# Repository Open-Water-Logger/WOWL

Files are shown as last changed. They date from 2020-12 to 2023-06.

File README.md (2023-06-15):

# WOWL
Hardware and Software Resources for the Wireless Open Water Logger (WOWL). 

Most current version is Gen 3. A detailed description of the casting process can be found on our blog at https://openwaterlogger.org/.

WOWL is a project of Creare working in collaboration with the Darling Marine Center at UMaine.

This project is supported by NOAA via SBIR contract NA20OAR0210323.

This project is licensed under the Apache License 2.0

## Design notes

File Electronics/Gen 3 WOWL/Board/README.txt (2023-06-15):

Schematic
1010403-900-0011_SCH_REV-B.pdf = schematic drawing

BOM
1010403-900-0010_BOM_REV_B.pdf - list of parts needed to build assemblies

PCB/Board
1010403-900-0012_rev-B-Gerbers.zip = Files to have PCB manufactured.
1010403-900-0012_FAB-REV-B.pdf = Fabrication drawing showing drill, dimensions, and stack-up.
1010403-900-0012_PCB_Rev-B_Placement.txt = component XY coordinates needed for part placement.
1010403-900-0012_rev-b-IPC-2581.zip - files required to have boards built at CircuitHub.

Can live with PCB/Board
1010403-900-0013_ASSY-REV-B.pdf = Assembly print showing Top and bottom component placement.

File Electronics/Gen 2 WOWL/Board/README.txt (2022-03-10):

PCB/Board
1010403-900-0012_rev-a-Gerbers.zip = Files to have PCB manufactured.
1010403-900-0012_rev-a.brd = OrCAD Design file PCB.
1010403-900-0012_rev-a_fab.pdf = Fabrication drawing showing drill, dimensions, and stack-up.
1010403-900-0012_PCB_Rev-A_Placement.txt = component XY coordinates needed for part placement.

Can live with PCB/Board
1010403-900-0013_ASB_Rev-A.pdf = Assembly print showing Bottom component placement.
1010403-900-0013_AST_Rev-A.pdf = Assembly print showing Top component placement.

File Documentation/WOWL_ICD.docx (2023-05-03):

# WOWL Interface Control Document

# 1 Introduction

The WOWL is a submersible temperature and pressure sensor and data logger. When on the surface, it provides communication via a Bluetooth interface. This document describes that interface.

## CRC32

This technology makes use of the CRC32 algorithm in several places. This is based on the implementation given in the PNG standard:

https://www.w3.org/TR/PNG/#D-CRCAppendix

# 2 WOWL Service

The WOWL device provides the WOWL service, on UUID 0x3090. At this time, the service provides eight characteristics.

## Pressure Offset, in Millibars (0x3091)

This 8-bit unsigned value is added to the pressure measurement. It can be used to trick the WOWL into thinking it is submerged, which is useful in generating records for testing. NOTE: at this time, the radio stays on while the device is submerged. When this is not the case, this characteristic will be removed, so as to prevent the device from becoming incommunicative forever.

## Record Count (0x3092)

This field returns the number of records stored in non-volatile memory, as a u16.

## Measurement Results (0x3093)

If the host device registers for notifications on this UUID, it will receive the incoming data at a rate of once per 10 seconds when the device is surfaced, and neither downloading or erasing data. All data are in LSB. See Table 1. The data will come in chunks of 20 bytes each, padded with zeros as needed.

Table 1. WOWL Measurement Data Format
Data Item | Format | Units
Measurement Count | u32 | Measurements
Status | u32 | See Table 2
Reserved | u32 | N/A
Charging Voltage | f32 | volts
Charging Current | f32 | amps
Rectified Charging Coil Voltage | f32 | volts
Battery Voltage | f32 | volts
CPU Temperature | f32 | °C
Temperature via NTC | f32 | °C
Temperature via RTD | f32 | °C
Temperature from SI7051-A20-IMR Digital Temperature Sensor | f32 | °C
Pressure | f32 | mbar
Temperature from Pressure Sensor | f32 | °C
Temperature of NTC ADC | f32 | °C
Temperature of RTD ADC | f32 | °C
CRC32 of fields above | u32 | N/A
Characteristic Length | 64 bytes | --

NOTE: Be sure to de-register the notifications before disconnecting.

Table 2. WOWL Status Bitfield
Bit | Meaning if Set
0 | Charging
1-7 | RESERVED
8 | Firmware Operation Complete
9 | Firmware Operation Failed
10-15 | RESERVED
16 | Connected to BLE
17 | Advertising for BLE
18-22 | RESERVED
23 | Last Command Unsupported
24 | Flash Failure
25 | SI7051 Temperature Sensor Failure
26 | Spurious I²C Event
27 | Pressure Sensor Failure
28-31 | RESERVED

## Record Download Request (0x3094)

This characteristic specifies which records are transmitted when a download is requested.

Table 3. WOWL Download Request
Field | Format | Units
Offset | u16 | Records
Count | u16 | Records
Characteristic Length | 4 bytes | --

## Record Download Data (0x3095)

This characteristic receives the downloaded records, if set to transmit notifications.

Table 4. WOWL Download Data
Data Item | Format | Units
Record Index | u16 | Records
Record Status | u16 | See Table 5
Record Data | SAMPLE | See Table 1
Characteristic Length | 68 bytes | --

The ‘Record Status’ field contains the result of the record retrieval process.

Table 5. WOWL Record Read Error Codes
Code | Description
0 | No Error
1 | Device Error
2 | Record is Blank
3 | CRC Mismatch
4-65535 | RESERVED

Note that the CRC field of the Record Data does not include the Record Index or Record Status fields.

## Commands (0x3096)

This u8 characteristic receives user commands. It must be written with the WriteCharValue GATT operation, not WriteLongCharValue. The commands are queued, and will only take effect when the device is at standby (i.e., not busy or submerged). The exception is the RESET command which takes effect immediately.

Table 2. WOWL Commands
Code | Description
0 | RESERVED
1 | Commence Download
2 | Start Erasure of Records
3 | Reset Processor
4 | DFU Setup
5 | DFU Write
6 | DFU Reprogram
7-255 | RESERVED

## DFU Setup (0x3097)

This characteristic is used to inform the WOWL about an upcoming firmware upgrade. The fields are given below.

Table 4. WOWL DFU Setup Fields
Data Item | Format | Units
Firmware Length | u32 | Bytes
CRC32 | u32 | N/A
Characteristic Length | 8 bytes | --

## DFU Data (0x3098)

This characteristic is used to store blocks of the firmware file, for commit by the device to program memory. The entire block should be used.

# 3 Stored Data Download Procedure

Here are the steps to download data from the WOWL.

1) Determine the appropriate number of records to download per request. A number smaller than “all of them” may be more robust. The author has tested up to 16.
2) Connect to the device.
3) Consult the Record Count characteristic.
4) Set the Record Download Request characteristic with the offset (initially zero) and count (determined in step 0, trimmed to the value in step 2).
5) Request notifications for the Record Download Data characteristic.
6) Set the Command characteristic to 1.
7) Repeat steps 3 through 5, increasing the offset appropriately each iteration. If data does not match the provided checksum, or the Record Index falls out of synchronicity, request that record again with a side request for that offset, count of one.
8) Cancel notifications of the Record Download Data characteristic.
9) Disconnect from the device.

# 4 Device Firmware Update (DFU) Procedure

Enumerated below are the suggested steps for reprogramming the WOWL.

1) Connect to the device.
2) Update the DFU Setup characteristic with the size of the firmware and its CRC32.
3) Send the DFU Setup command.
4) Wait one second for the device to erase the temporary storage area.
5) Write the first data block to the DFU Data characteristic.
6) Send the DFU Write command.
7) Repeat steps 5 and 6 until all the firmware is written.
8) Send the DFU Reprogram command. If successful, the device will reset itself and the Bluetooth connection will be severed.
9) After a short wait the device will be available for reconnection.
10) The ‘Firmware Revision String’, part of the Device Information Service, at UUID 0x2A26, will contain the software build date and time.

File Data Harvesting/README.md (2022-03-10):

# Python WOWL downloader

Python script to download WOWL data ---> read_wowl.py.

read_wowl.py contains the functions that can connect to a WOWL and download the data. Sending data to server and location is currently not supported.

There seems to be a bug with the python bluetooth module (bleak) for Windows and code may error when connecting. We are working to fix this and it might run on other OS although it is untested.

More documentation and functionality for this code base will continue to be added.

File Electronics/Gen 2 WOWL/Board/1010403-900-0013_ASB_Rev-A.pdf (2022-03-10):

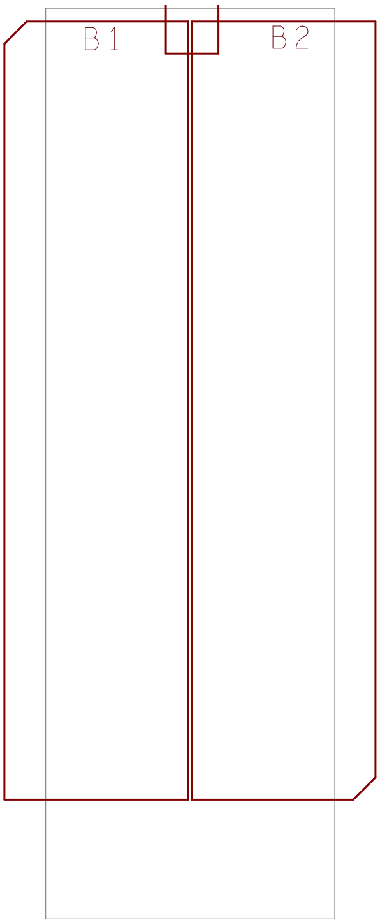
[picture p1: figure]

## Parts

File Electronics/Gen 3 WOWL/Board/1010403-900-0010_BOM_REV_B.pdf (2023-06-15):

WOWL Board Assembly/BOM
Project: | 1010403 Gone Fishing
Part #: | 1010403-900-0010 | Release 10/19/2022 RWM
Revision: | B
Item | Quantity | Reference | Description | Manufacturer | Manufacturer Part# | Suggested Vendor | Suggested Vendor Part # | Footprint | Temp Min | Temp Max
1 | 1 | DOC | Schematic | Creare | 1010403-900-0011, Rev.B | N/A | N/A | N/A | N/A | N/A
2 | 1 | PCB | PCB | | 1010403-900-0012, Rev.B | N/A | N/A | N/A | N/A | N/A
3 | 1 | ANT1 | PCB Antenna, 2.4GHz | DNP | DNP | DNP | DNP | pcbantenna_an043 | - | -
4 | 2 | B1 B2 | BATTERY NIMH 1.2V 700MAH AAA | Panasonic - BSG | HHR70AAAB8T | Digi-Key | P213T-ND | PANASONIC_HHR70AAAB8T | -10°C | 65°C
5 | 10 | C1 C4 C6 C10 C14 C15 C21 C40 C42 C55 0.1uF, 50V, 10%, X7R, Ceramic, 0402 | | TDK | CGA2B3X7R1H104K050BB | Digi-Key | 445-6899-1-ND | CAPC100X50X55L20N | -55°C | 125°C
6 | 1 | C2 | 10uF, 10V, 20%, X5R, Ceramic, 0402 | Samsung | CL05A106MP8NUB8 | Digi-Key | 1276-6830-1-ND | CAPC100X50X90L25N | -55°C | 85°C
7 | 1 | C11 | DNP, 10uF, 10V, 20%, X5R, Ceramic, 0402 | | | | | CAPC100X50X90L25N | -55°C | 85°C
8 | 1 | C12 | 22uF, 25V, 20%, X5R, Ceramic, 0805 | TDK Corporation | C2012X5R1E226M125AC | Digi-Key | 445-9112-1-ND | CAPC2013X145N | -55°C | 85°C
9 | 2 | C16 C58 | DNP, Capacitor, 0402 | NA | NA | NA | NA | CAPC1005X55L25N
10 | 1 | C19 | 0.8pF, 50V, ±0.1pF, NP0, Ceramic, 0402 | Murata | GJM1555C1HR80BB01D | Digi-Key | 490-6080-1-ND | CAPC100X50X55L25N | -55°C | 125°C
11 | 2 | C22 C25 | 22nF, 50V, 10%, X7R, Ceramic, 0402 | Murata Electronics North America GRM155R71H223KA12D | | Digi-Key | 490-3884-1-ND | CAPC100X50X55L25N | -55°C | 125°C
12 | 4 | C23 C24 C27 C28 | 12pF, 50V, 1%, NP0, Ceramic, 0402 | Murata | GJM1555C1H120FB01D | Digi-Key | 490-11190-1-ND | CAPC100X50X55L25N | -55°C | 125°C
13 | 2 | C26 C44 | 0.47uF, 25V, 10%, X5R, Ceramic, 0402 | TDK | C1005X5R1E474K050BB | Digi-Key | 445-8020-1-ND | CAPC100X50X55L15N | -55°C | 85°C
14 | 1 | C32 | 15nF, 100V, 10%, X7R, Ceramic, 0603 | Murata | GCM188R72A153KA37D | Digi-Key | 490-8029-1-ND | CAPC160X80X90L35N | -55°C | 125°C
15 | 3 | C41 C43 C56 | 1uF, 25V, 10%, X5R, Ceramic, 0603 | AVX | 06033D105KAT2A | Digi-Key | 478-5142-1-ND | CAPC1608X94N | -55°C | 85°C
16 | 2 | C45 C46 | 10nF, 50V, 10%, X8R, Ceramic, 0402 | TDK | C1005X8R1H103K050BB | Digi-Key | 445-8851-1-ND | CAPC100X50X55L15N | -55°C | 150°C
17 | 2 | C47 C48 | 68nF, 50V, 5%, X7R, Ceramic, 0603 | Kemet | C0603C683J5RACTU | Digi-Key | 399-9121-1-ND | CAPC160X80X87L35N | -55°C | 125°C
18 | 1 | C49 | 47nF, 50V, 10%, X7R, Ceramic, 0402 | TDK | CGA2B3X7R1H473K050BB | Digi-Key | 445-6897-1-ND | CAPC100X50X55L20N | -55°C | 125°C
19 | 1 | C50 | 1.8nF, 50V, 10%, X7R, Ceramic, 0402 | AVX | 04025C182KAT2A | Digi-Key | 478-1104-1-ND | CAPC100X50X56L25N | -55°C | 125°C
20 | 1 | C51 | 100pF, 50V, 5%, C0G, Ceramic, 0603 | KEMET | C0603T101J5GCLTU | Digi-Key | 399-6300-1-ND | CAPC160X80X87L35N | -55°C | 125°C
21 | 1 | C52 | 0.1uF, 50V, 10%, X7R, Ceramic, 0603 | AVX | 06035C104KAZ2A | Digi-Key | 478-3540-1-ND | CAPC1608X94N | -55°C | 125°C
22 | 2 | C53 C54 | 10uF, 35V, 20%, X5R, Ceramic, 0603 | Murata | GRM188R6YA106MA73D | Digi-Key | 490-13248-1-ND | CAPC160X80X100L37N | -55°C | 85°C
23 | 1 | C57 | 100pF, 50V, 1%, C0G, Ceramic, 0402 | AVX | 04025A101FAT2A | Digi-Key | 478-3658-1-ND | CAPC100X50X56L25N | -55°C | 125°C
24 | 1 | D1 | LED, Green, 2.1V, 20mA | SunLED | XZVG54W-8 | Digi-Key | 1497-1434-1-ND | LEDC200X125X120L40N | -40°C | 85°C
25 | 1 | D2 | LED Red/Yel, 2.2V/2V, 20mA, 1206 | SunLED | XZM2CRKCYK55W-8 | Digi-Key | 1497-1306-1-ND | SUNLED_XZM2CRKCYK55W-8 | -40°C | 85°C
26 | 1 | D3 | LED, Green, 2.1V, 10mA, 3.2mcd, 0603 | Lite-On Inc. | LTST-C190GKT | Digi-Key | 160-1183-1-ND | LEDC1608X80N | -55°C | 85°C
27 | 1 | F1 | Fuse, 2A, 63VDC, Slow, 1206 | Bourns | SF-1206SP200M-2 | Digi-Key | SF-1206SP200M-2CT-ND | FUSC320X160X117L51N | -55°C | 150°C
28 | 1 | J1 | FFC/FPC, 6pos, 0.5mm, 0.5A, 50V, R/A, SMD | Molex | 5034800600 | Digi-Key | WM1387CT-ND | Molex_503480-0600 | -40°C | 85°C
29 | 1 | L1 | 3.9nH, 400mA, High Frequency, 0402 | TDK | MLK1005S3N9ST000 | Digi-Key | 445-1462-1-ND | INDC1005X60L15 | -55°C | 125°C
30 | 1 | L2 | 10uH, 100mA, Wirewound, 0603 | Abracon | AISC-0603F-100J-T | Digi-Key | 535-12537-1-ND | Abracon_AISC-0603F | -40°C | 85°C
31 | 1 | L3 | 15nH, 300mA, High Frequency, 0402 | TDK | MLK1005S15NJT000 | Digi-Key | 445-1469-1-ND | INDC1005X60L15 | -55°C | 125°C
32 | 1 | Q2 | MOSFET, P-CH, 20V, 3.6A, SOT-23 | Diodes | DMP2035U-7 | Digi-Key | DMP2035U-7DICT-ND | SOT23-3P91_240X120L53X44 | -55°C | 150°C
33 | 1 | R1 | 100K, 1%, 50V, 1/16W, Thick, 0402 | Vishay | CRCW0402100KFKED | Digi-Key | 541-100KLCT-ND | RESC100X50X40L25 | -55°C | 155°C
34 | 1 | R2 | 4.99K, 1%, 50V, 1/16W, Thick, 0402 | Vishay | CRCW04024K99FKED | Digi-Key | 541-4.99KLCT-ND | RESC100X50X40L25 | -55°C | 155°C
35 | 1 | R4 | DNP, 4.99K, 1%, 50V, 1/16W, Thick, 0402 | | | | | RESC100X50X40L25 | -55°C | 155°C
36 | 1 | R5 | 140 Ohms, 1%, 75V, 1/10W, Thick, 0603 | Vishay | CRCW0603140RFKEA | Digi-Key | 541-140HCT-ND | RESC155X85X50L30N | -55°C | 155°C
37 | 4 | R7 R8 R9 R12 | 33 Ohms, 1%, 50V, 1/10W, Thick, 0402 | Panasonic | ERJ-2RKF33R0X | Digi-Key | P33.0LCT-ND | RESC100X50X40L25 | -55°C | 155°C
38 | 4 | R10 R19 R26 R33 | 10K, 1%, 50V, 1/10W, Thick, 0402 | Panasonic Electronic Components ERJ-2RKF1002X | | Digi-Key | P10.0KLCT-ND | RESC100X50X40L25 | -55°C | 155°C
39 | 4 | R11 R35 R36 R37 | 1M, 1%, 50V, 1/10W, Thick, 0402 | Panasonic | ERJ-2RKF1004X | Digi-Key | P1.00MLCT-ND | RESC100X50X40L25 | -55°C | 155°C
40 | 1 | R13 | DNP, Jumper, 50V, 1/16W, Thick, 0402 | Vishay | CRCW04020000Z0ED | Digi-Key | 541-0.0JCT-ND | RESC100X50X40L25 | -55°C | 155°C
41 | 1 | R14 | 10K, 1%, 50V, 1/16W, Thick, 0402 | Vishay | CRCW040210K0FKED | Digi-Key | 541-10.0KLCT-ND | RESC100X50X40L25 | -55°C | 155°C
42 | 1 | R15 | 357 Ohms, 1%, 75V, 1/10W, Thick, 0603 | Vishay | CRCW0603357RFKEA | Digi-Key | 541-357HCT-ND | RESC155X85X50L30N | -55°C | 155°C
43 | 1 | R16 | 1.5K, 5%, 75V, 1/10W, Thick, 0603 | Vishay | CRCW06031K50JNEA | Digi-Key | 541-1.5KGCT-ND | RESC155X85X50L30N | -55°C | 155°C
44 | 2 | R17 R20 | 1M, 1%, 50V, 1/16W, Thick, 0402 | KOA Speer | RK73H1ETTP1004F | Mouser | 660-RK73H1ETTP1004F | RESC1005X40N | -55°C | 155°C
45 | 3 | R22 R34 R39 | 100 Ohms, 1%, 50V, 1/10W, Thick, 0402 | Panasonic | ERJ-2RKF1000X | Digi-Key | P100LCT-ND | RESC100X50X40L25 | -55°C | 155°C
46 | 1 | R30 | 140K, 1%, 50V, 1/10W, Thick, 0402 | Panasonic | ERJ-2RKF1403X | Digi-Key | P140KLCT-ND | RESC100X50X40L25 | -55°C | 155°C
47 | 1 | R31 | 100K, 1%, 50V, 1/10W, Thick, 0402 | Panasonic | ERJ-2RKF1003X | Digi-Key | P100KLCT-ND | RESC100X50X40L25 | -55°C | 155°C
48 | 1 | R38 | DNP, 100K, 1%, 150V, 1/8W, Thick, 0805 | Vishay | DNP(CRCW0805100KFKEA) | | | RESC205X125X50L35N | -55°C | 155°C
49 | 2 | R44 R45 | 4.02K, 1%, 50V, 1/10W, Thick, 0402 | Panasonic | ERJ-2RKF4021X | Digi-Key | P4.02KLCT-ND | RESC100X50X40L25 | -55°C | 155°C
50 | 1 | R51 | Jumper, 50V, 1/16W, Thick, 0402 | Vishay | CRCW04020000Z0ED | Digi-Key | 541-0.0JCT-ND | RESC100X50X40L25 | -55°C | 155°C
51 | 1 | RT2 | Thermistor, NTC, 10K, Max Temp 125°C,TH | Cantherm | MF52A2103J3470 | Digi-Key | 317-1258-ND | THRMRB220W45L300T300H950 | -55°C | 125°C
52 | 1 | SW1 | Switch, Reed, SPST-NO, 100mA, 30V, SM | Standex | MK24-A-3 | Digi-Key | 374-1138-1-ND | standex_mk24-a-3 | -40°C | 115°C
53 | 12 | TP7 TP8 TP9 TP12 TP19 TP20 TP21 TP23 TP24 TP25 TP26 TP27 DNP, Test Point, SMD, 25 mil Round Pad | | NA | NA | NA | NA | TP_C0635 | NA | NA
54 | 2 | TP28 TP29 | Test Point, Miniature, 3.4mm x 1.8mm Pad, SMD | Keystone | 5015 | Digi-Key | 36-5015CT-ND | TP340X180N
55 | 1 | U1 | Temperature, Digital, -40~125°C, 6WDFN | TI | TMP117AIDRVR | Digi-Key | 296-51834-1-ND | son7p65_200x200x80l25x30t160x100n-55°C | | 150°C
56 | 1 | U10 | Buffer, Triple, Open Drain, 8XSON | Nexperia USA Inc. | 74LVC3G07GS,115 | Digi-Key | 1727-8082-1-ND | PSON8P35_135X100X35L31X16N | -40°C | 125°C
57 | 1 | U2 | Pressure Sensor, 0 ~30bar, ±400 mbar, I2C, SMD | TE Connectivity Measurement Specialties MS583730BA01-50 | | Digi-Key | 223-1704-1-ND | icdfn4_330x330x285l130x130 | -20°C | 85°C
58 | 1 | U3 | Buffer, Single, Open Drain, 6-SON | TI | SN74LVC1G07QDRYRQ1 | Digi-Key | 296-SN74LVC1G07QDRYRQ1CT-ND pson6p50_145x100x55l30x20n | | -40°C | 125°C
59 | 1 | U5 | SOC, 2.4 GHz Bluetooth, Cortex M4 MCU, 512K Flash, 64K RAM, 48QFN Nordic | | NRF52832-QFAA-R | Digi-Key | 1490-1052-1-ND | QFN40P600X600X90-49N | -40°C | 85°C
60 | 1 | U6 | Flash Memory, 16Mbit, 80MHz, 8USON | Macronix | MX25R1635FZUIH0 | Digi-Key | 1092-1178-1-ND | PSON9P50_200X300X60L40X25T160X20N -40°C | | 85°C
61 | 1 | U7 | Battery Charger, Multi-Chemistry, 60V, 250mA, 10DFN Analog Devices Inc. | | LTC4079EDD#TRPBF | Digi-Key | LTC4079EDD#TRPBFCT-ND | SON11P50_300X300X80L40X25T238X165N -40°C | | 125°C
62 | 1 | U8 | Wireless Power Supply Receiver, 20QFN | Texas Instruments | BQ51013ARHLR | Digi-Key | 296-30568-1-ND | QFN50P450X350X100-21N | 0°C | 125°C
63 | 1 | U9 | Opamp, Single, GP, RRIO, 6.2kHz, SC70-5 | Texas Instruments | LPV521MG/NOPB | Digi-Key | 296-39069-1-ND | SOT23-5P65_210X110L36X22N | -40°C | 125°C
64 | 1 | Y2 | Crystal, 32MHz, 8pF, SMD | ECS | ECS-320-8-37CKM | Digi-Key | XC1547CT-ND | OSCCC200X160X46-4NA | -20°C | 70°C
65 | 1 | Y4 | Crystal, 32.768kHz, 9pF, SMD | Abracon | ABS05-32.768KHZ-9-T | Digi-Key | 535-11897-1-ND | DFN160X100X50-2NA | -40°C | 85°C
66 | 1 | L4 | Coil | TDK | WR303050-15F5-G | Digi-Key | 445-16092-ND | N/A

Part Supplied by Creare
DNP = Do Not Populate
Additional Assembly Required/Part Supplied by Creare
WOWL Board Assembly/BOM | Page 1 of 1

1010403-900-0010
Rev. B

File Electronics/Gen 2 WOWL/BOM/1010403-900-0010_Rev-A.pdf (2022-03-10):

WOWL Board Assembly/BOM
Project: | 1010403 Gone Fishing
Part #: | 1010403-900-0010 | Released 02/22/2022 RWM
Revision: | A
Item | Quantity | Reference | Description | Manufacturer | Manufacturer Part# | Suggested Vendor | Suggested Vendor Part # | Footprint | Temp Min | Temp Max
1 | 1 | DOC | Schematic | Creare | 1010403-900-0011, Rev.A | N/A | N/A | N/A | N/A | N/A
2 | 1 | PCB | PCB | | 1010403-900-0012, Rev.A | N/A | N/A | N/A | N/A | N/A
3 | 1 | ANT1 | PCB Antenna, 2.4GHz | DNP | DNP | DNP | DNP | pcbantenna_an043 | - | -
4 | 2 | B1 B2 | BATTERY NIMH 1.2V 700MAH AAA | Panasonic - BSG | HHR70AAAB8T | Digi-Key | P213T-ND | PANASONIC_HHR70AAAB8T | -10°C | 65°C
5 | 15 | C1 C3 C4 C5 C7 C8 C10 C12 C13 C14 C15 C40 C42 C43 C55 | 0.1uF, 50V, 10%, X7R, Ceramic, 0402 | TDK | CGA2B3X7R1H104K050BB | Digi-Key | 445-6899-1-ND | CAPC100X50X55L20N | -55°C | 125°C
6 | 1 | C2 | 10uF, 10V, 20%, X5R, Ceramic, 0402 | Samsung | CL05A106MP8NUB8 | Digi-Key | 1276-6830-1-ND | CAPC100X50X90L25N | -55°C | 85°C
7 | 1 | C11 | DNP 10uF, 10V, 20%, X5R, Ceramic, 0402 | Samsung | CL05A106MP8NUB8 | Digi-Key | 1276-6830-1-ND | CAPC100X50X90L25N | -55°C | 85°C
8 | 1 | C6 | 4.7uF, 10V, 10%, X5R, Ceramic, 0402 | Murata | ZRB15XR61A475KE01D | Digi-Key | 490-13252-1-ND | CAPC100X50X80L25N | -55°C | 85°C
9 | 1 | C9 | 4.7uF, 10V, 10%, X5R, Ceramic, 0402 | TDK | C1005X5R1A475K050BC | Digi-Key | 445-13820-1-ND | CAPC102X52X65L15N | -55°C | 85°C
10 | 1 | C16 | 3.4pF, 50V, ±0.1pF, C0G, Ceramic, 0402 | KEMET | CBR04C349B5GAC | Digi-Key | 399-16077-1-ND | CAPC100X50X55L22N | -55°C | 125°C
11 | 1 | C17 | 0.22uF, 35V, 10%, X7R, Ceramic, 0402 | TDK | C1005X7R1V224K050BE | Digi-Key | 445-173778-1-ND | CAPC100X50X60L15N | -55°C | 125°C
12 | 1 | C18 | 1.2PF, 50V, ±0.05pF, C0G, Ceramic, 0402 | Murata | GJM1555C1H1R2WB01D | Digi-Key | 490-11195-1-ND | CAPC100X50X55L25N | -55°C | 125°C
13 | 1 | C19 | 0.5pF, 50V, ±0.1pF, C0G, Ceramic, 0402 | Murata | GJM1555C1HR50BB01D | Digi-Key | 490-6077-1-ND | CAPC100X50X55L25N | -55°C | 125°C
14 | 2 | C20 C21 | DNP, 1uF, 10V, 10%, X7S, Ceramic, 0402 | TDK | C1005X7S1A105K050BC | Digi-Key | 445-9116-1-ND | CAPC100X50X55L15N | -55°C | 125°C
15 | 2 | C22 C25 | 22nF, 50V, 10%, X7R, Ceramic, 0402 | Murata Electronics North America GRM155R71H223KA12D | | Digi-Key | 490-3884-1-ND | CAPC100X50X55L25N | -55°C | 125°C
16 | 2 | C23 C24 | DNP 12pF, 50V, 1%, NP0, Ceramic, 0402 | Murata | GJM1555C1H120FB01D | Digi-Key | 490-11190-1-ND | CAPC100X50X55L25N | -55°C | 125°C
17 | 2 | C27 C28 | 12pF, 50V, 1%, NP0, Ceramic, 0402 | Murata | GJM1555C1H120FB01D | Digi-Key | 490-11190-1-ND | CAPC100X50X55L25N | -55°C | 125°C
18 | 2 | C26 C44 | 0.47uF, 25V, 10%, X5R, Ceramic, 0402 | TDK | C1005X5R1E474K050BB | Digi-Key | 445-8020-1-ND | CAPC100X50X55L15N | -55°C | 85°C
19 | 1 | C32 | 15nF, 100V, 10%, X7R, Ceramic, 0603 | Murata | GCM188R72A153KA37D | Digi-Key | 490-8029-1-ND | CAPC160X80X90L35N | -55°C | 125°C
20 | 1 | C41 | 1uF, 25V, 10%, X5R, Ceramic, 0603 | AVX Corporation | 06033D105KAT2A | Digi-Key | 478-5142-1-ND | CAPC1608X94N | -55°C | 85°C
21 | 2 | C45 C46 | 10nF, 50V, 10%, X8R, Ceramic, 0402 | TDK Corporation | C1005X8R1H103K050BB | Digi-Key | 445-8851-1-ND | CAPC100X50X55L15N | -55°C | 150°C
22 | 2 | C47 C48 | 68nF, 50V, 5%, X7R, Ceramic, 0603 | Kemet | C0603C683J5RACTU | Digi-Key | 399-9121-1-ND | CAPC160X80X87L35N | -55°C | 125°C
23 | 1 | C49 | 47nF, 50V, 10%, X7R, Ceramic, 0402 | TDK | CGA2B3X7R1H473K050BB | Digi-Key | 445-6897-1-ND | CAPC100X50X55L20N | -55°C | 125°C
24 | 1 | C50 | 1.8nF, 50V, 10%, X7R, Ceramic, 0402 | AVX | 04025C182KAT2A | Digi-Key | 478-1104-1-ND | CAPC100X50X56L25N | -55°C | 125°C
25 | 1 | C51 | 100pF, 50V, 5%, C0G, Ceramic, 0603 | KEMET | C0603T101J5GCLTU | Digi-Key | 399-6300-1-ND | CAPC160X80X87L35N | -55°C | 125°C
26 | 1 | C52 | 0.1uF, 50V, 10%, X7R, Ceramic, 0603 | AVX | 06035C104KAZ2A | Digi-Key | 478-3540-1-ND | CAPC1608X94N | -55°C | 125°C
27 | 2 | C53 C54 | 10uF, 35V, 20%, X5R, Ceramic, 0603 | Murata | GRM188R6YA106MA73D | Digi-Key | 490-13248-1-ND | CAPC160X80X100L37N | -55°C | 85°C
28 | 1 | D1 | LED, Green, 2.1V, 20mA | SunLED | XZVG54W-8 | Digi-Key | 1497-1434-1-ND | LEDC200X125X120L40N | -40°C | 85°C
29 | 1 | D2 | LED Red/Yel, 2.2V/2V, 20mA, 1206 | SunLED | XZM2CRKCYK55W-8 | Digi-Key | 1497-1306-1-ND | SUNLED_XZM2CRKCYK55W-8 | -40°C | 85°C
30 | 1 | D3 | LED, Green, 2.1V, 10mA, 3.2mcd, 0603 | Lite-On Inc. | LTST-C190GKT | Digi-Key | 160-1183-1-ND | LEDC1608X80N | -55°C | 85°C
31 | 1 | F1 | DNP Fuse, 2A, 63VDC, Slow, 1206 | Bourns | SF-1206SP200M-2 | Digi-Key | SF-1206SP200M-2CT-ND | FUSC320X160X117L51N | -55°C | 150°C
32 | 1 | J1 | FFC/FPC, 6pos, 0.5mm, 0.5A, 50V, R/A, SMD | Molex | 5034800600 | Digi-Key | WM1387CT-ND | Molex_503480-0600 | -40°C | 85°C
33 | 1 | L1 | 3.3nH, 2A, High Freq., Wirewound, 0402 | Murata | LQW15AN3N3B80D | Digi-Key | 490-7641-1-ND | INDC100X60X60L20N | -55°C | 125°C
34 | 1 | L2 | 22nH, 350mA, High Frequency, 0402 | Murata | LQG15HS22NH02D | Digi-Key | 490-15112-1-ND | INDC100X50X55L25N | -55°C | 125°C
35 | 1 | L3 | 10uH, 200mA, 1.2 OHM, 0603 | KEMET | L0603B100KPWFT | Digi-Key | 399-17789-1-ND | indc160x80x90l35n | -40°C | 105°C
36 | 1 | Q2 | MOSFET, P-CH, 20V, 3.6A, SOT-23 | Diodes | DMP2035U-7 | Digi-Key | DMP2035U-7DICT-ND | SOT23-3P91_240X120L53X44 | -55°C | 150°C
37 | 1 | R1 | DNP, 100K, 1%, 150V, 1/8W, Thick, 0805 | Vishay | DNP(CRCW0805100KFKEA) | | | RESC205X125X50L35N | -55°C | 155°C
38 | 1 | R2 | 100K, 1%, 50V, 1/16W, Thick, 0402 | Vishay | CRCW0402100KFKED | Digi-Key | 541-100KLCT-ND | RESC100X50X40L25 | -55°C | 155°C
39 | 1 | R3 | 4.99K, 1%, 50V, 1/16W, Thick, 0402 | Vishay | CRCW04024K99FKED | Digi-Key | 541-4.99KLCT-ND | RESC100X50X40L25 | -55°C | 155°C
40 | 1 | R4 | 4.99K, 1%, 50V, 1/16W, Thick, 0402 | Vishay | CRCW04024K99FKED | Digi-Key | 541-4.99KLCT-ND | RESC100X50X40L25 | -55°C | 155°C
41 | 1 | R5 | 140 Ohms, 1%, 75V, 1/10W, Thick, 0603 | Vishay Dale | CRCW0603140RFKEA | Digi-Key | 541-140HCT-ND | RESC1609X50N | -55°C | 155°C
42 | 1 | R6 | Jumper, 50V, 1.5A, Thick, 0402 | Stackpole | RMCF0402ZT0R00 | Digi-Key | RMCF0402ZT0R00CT-ND | RESC100X50X40L25 | -55°C | 155°C
43 | 4 | R7 R8 R9 R12 | 33 Ohms, 1%, 50V, 1/10W, Thick, 0402 | Panasonic | ERJ-2RKF33R0X | Digi-Key | P33.0LCT-ND | RESC100X50X40L25 | -55°C | 155°C
44 | 4 | R10 R19 R26 R33 | 10K, 1%, 50V, 1/10W, Thick, 0402 | Panasonic Electronic Components ERJ-2RKF1002X | | Digi-Key | P10.0KLCT-ND | RESC100X50X40L25 | -55°C | 155°C
45 | 4 | R11 R35 R36 R37 | 1M, 1%, 50V, 1/10W, Thick, 0402 | Panasonic | ERJ-2RKF1004X | Digi-Key | P1.00MLCT-ND | RESC100X50X40L25 | -55°C | 155°C
46 | 1 | R13 | DNP, Jumper, 50V, 1/16W, Thick, 0402 | Vishay | CRCW04020000Z0ED | Digi-Key | 541-0.0JCT-ND | RESC100X50X40L25 | -55°C | 155°C
47 | 1 | R14 | 10K, 1%, 50V, 1/16W, Thick, 0402 | Vishay | CRCW040210K0FKED | Digi-Key | 541-10.0KLCT-ND | RESC100X50X40L25 | -55°C | 155°C
48 | 1 | R15 | 357 Ohms, 1%, 75V, 1/10W, Thick, 0603 | Vishay | CRCW0603357RFKEA | Digi-Key | 541-357HCT-ND | RESC155X85X50L30N | -55°C | 155°C
49 | 1 | R16 | 1.5K, 5%, 75V, 1/10W, Thick, 0603 | Vishay Dale | CRCW06031K50JNEA | Digi-Key | 541-1.5KGCT-ND | RESC1609X50N | -55°C | 155°C

Part Supplied by Creare
DNP = Do Not Populate
WOWL Board Assembly/BOM | Page 1 of 2

1010403-900-0010
Rev. A

50 | 2 | R17 R20 | 1M, 1%, 50V, 1/16W, Thick, 0402 | KOA Speer | RK73H1ETTP1004F | Mouser | 660-RK73H1ETTP1004F | RESC1005X40N | -55°C | 155°C
51 | 3 | R22 R34 R39 | 100 Ohms, 1%, 50V, 1/10W, Thick, 0402 | Panasonic | ERJ-2RKF1000X | Digi-Key | P100LCT-ND | RESC100X50X40L25 | -55°C | 155°C
52 | 1 | R30 | 140K, 1%, 50V, 1/10W, Thick, 0402 | Panasonic | ERJ-2RKF1403X | Digi-Key | P140KLCT-ND | RESC100X50X40L25 | -55°C | 155°C
53 | 1 | R31 | 100K, 1%, 50V, 1/10W, Thick, 0402 | Panasonic | ERJ-2RKF1003X | Digi-Key | P100KLCT-ND | RESC100X50X40L25 | -55°C | 155°C
54 | 2 | R44 R45 | 4.02K, 1%, 50V, 1/10W, Thick, 0402 | Panasonic | ERJ-2RKF4021X | Digi-Key | P4.02KLCT-ND | RESC100X50X40L25 | -55°C | 155°C
55 | 1 | RT2 | Thermistor, NTC, 10K, Max Temp 125°C,TH | Cantherm | MF52A2103J3470 | Digi-Key | 317-1258-ND | THRMRB220W45L300T300H950 | -55°C | 125°C
56 | 1 | SW1 | Switch, Reed, SPST-NO, 100mA, 30V, SM | Standex | MK24-A-3 | Digi-Key | 374-1138-1-ND | standex_mk24-a-3 | -40°C | 115°C
57 | 12 | TP1 TP2 TP3 TP7 | DNP, Test Point, SMD, 25 mil Round Pad | NA | NA | NA | NA | TP_C0635
58 | 2 | TP28 TP29 | Test Point, Miniature, 3.4mm x 1.8mm Pad, SMD | Keystone | 5015 | Digi-Key | 36-5015CT-ND | TP340X180N
59 | 1 | U1 | Temperature, Digital, -40~125°C, 6WDFN | TI | TMP117AIDRVR | Digi-Key | 296-51834-1-ND | son7p65_200x200x80l25x30t160x100n-55°C | | 150°C
60 | 1 | U10 | Buffer, Triple, Open Drain, 8XSON | Nexperia USA Inc. | 74LVC3G07GS,115 | Digi-Key | 1727-8082-1-ND | PSON8P35_135X100X35L31X16N | -40°C | 125°C
61 | 1 | U2 | Pressure Sensor, 0 ~30bar, ±400 mbar, I2C, SMD | TE Connectivity Measurement Specialties MS583730BA01-50 | | Digi-Key | 223-1704-1-ND | icdfn4_330x330x285l130x130 | -20°C | 85°C
62 | 1 | U3 | RF Filter, Low Pass, 2.45GHZ Center, 4SMD | TDK | DLF162500LT-5028A1 | Digi-Key | 445-15658-1-ND | tdk_dlf162500lt-5028a1 | -40°C | 85°C
63 | 1 | U4 | IC BUFFER NON-INVERT 5.5V 6USON | TI | SN74LVC1G07QDRYRQ1 | Digi-Key | 296-SN74LVC1G07QDRYRQ1CT-NDpson6p50_145x100x55l30x20n | -40C ~ 125C (TA)
64 | 1 | U5 | SOC, 2.4 GHz Bluetooth, Cortex-M0+ MCU, 256K Flash, 64K RAM, 48QFN STMicro | | BLUENRG-355MT | Mouser | 511-BLUENRG-355MT | QFN49P40_600X600X105L40X21T450N-40°C | | 105°C
65 | 1 | U6 | Flash Memory, 16Mbit, 80MHz, 8USON | Macronix | MX25R1635FZUIH0 | Digi-Key | 1092-1178-1-ND | PSON9P50_200X300X60L40X25T160X20N -40°C | | 85°C
66 | 1 | U7 | Battery Charger, Multi-Chemistry, 60V, 250mA, 10DFN Analog Devices Inc. | | LTC4079EDD#TRPBF | Digi-Key | LTC4079EDD#TRPBFCT-ND | SON11P50_300X300X80L40X25T238X165N -40°C | | 125°C
67 | 1 | U8 | Wireless Power Supply Receiver, 20QFN | Texas Instruments | BQ51013ARHLR | Digi-Key | 296-30568-1-ND | QFN50P450X350X100-21N | 0°C | 125°C
68 | 1 | U9 | Opamp, Single, GP, RRIO, 6.2kHz, SC70-5 | Texas Instruments | LPV521MG/NOPB | Digi-Key | 296-39069-1-ND | SOT23-5P65_210X110L36X22N | -40°C | 125°C
69 | 1 | Y2 | Crystal, 32MHz, 8pF, SMD | ECS | ECS-320-8-37CKM | Digi-Key | XC1547CT-ND | OSCCC200X160X46-4NA | -20°C | 70°C
70 | 1 | Y4 | Crystal, 32.768kHz, 9pF, SMD | Abracon | ABS05-32.768KHZ-9-T | Digi-Key | 535-11897-1-ND | DFN160X100X50-2NA | -40°C | 85°C
71 | 1 | L4 | Coil | TDK | WR303050-15F5-G | Digi-Key | 445-16092-ND | N/A
WOWL Board Assembly/BOM | Page 2 of 2

1010403-900-0010
Rev. A

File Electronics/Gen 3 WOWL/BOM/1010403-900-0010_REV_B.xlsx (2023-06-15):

WOWL Board Assembly/BOM
Project: | WOWL
Part #: | 1010403-900-0010 |  | Release 10/19/2022 RWM
Revision: | B
Item | Quantity | Reference | Description | Manufacturer | Manufacturer Part# | Suggested Vendor | Suggested Vendor Part # | Footprint | Temp Min | Temp Max
1 | 1 | DOC | Schematic | Creare | 1010403-900-0011, Rev.B | N/A | N/A | N/A | N/A | N/A
2 | 1 | PCB | PCB |  | 1010403-900-0012, Rev.B | N/A | N/A | N/A | N/A | N/A
3 | 1 | ANT1 | PCB Antenna, 2.4GHz | DNP | DNP | DNP | DNP | pcbantenna_an043 | - | - |  | TMP-5069
4 | 2 | B1 B2 | BATTERY NIMH 1.2V 700MAH AAA | Panasonic - BSG | HHR70AAAB8T | Digi-Key | P213T-ND | PANASONIC_HHR70AAAB8T | -10°C | 65°C | 27 | HHR70AAAB8T
5 | 10 | C1 C4 C6 C10 C14 C15 C21 C40 C42 C55 | 0.1uF, 50V, 10%, X7R, Ceramic, 0402 | TDK | CGA2B3X7R1H104K050BB | Digi-Key | 445-6899-1-ND | CAPC100X50X55L20N | -55°C | 125°C | 1427408 | CGA2B3X7R1H104K050BB
6 | 1 | C2 | 10uF, 10V, 20%, X5R, Ceramic, 0402 | Samsung | CL05A106MP8NUB8 | Digi-Key | 1276-6830-1-ND | CAPC100X50X90L25N | -55°C | 85°C | 3619004 | CL05A106MP8NUB8
7 | 1 | C11 | DNP, 10uF, 10V, 20%, X5R, Ceramic, 0402 |  |  |  |  | CAPC100X50X90L25N | -55°C | 85°C |  | DNP
8 | 1 | C12 | 22uF, 25V, 20%, X5R, Ceramic, 0805 | TDK Corporation | C2012X5R1E226M125AC | Digi-Key | 445-9112-1-ND | CAPC2013X145N | -55°C | 85°C | 0 | C2012X5R1E226M125AC
9 | 2 | C16 C58 | DNP, Capacitor, 0402 | NA | NA | NA | NA | CAPC1005X55L25N |  |  |  | DNP_CAP_0402
10 | 1 | C19 | 0.8pF, 50V, ±0.1pF, NP0, Ceramic, 0402 | Murata | GJM1555C1HR80BB01D | Digi-Key | 490-6080-1-ND | CAPC100X50X55L25N | -55°C | 125°C | 266571 | GJM1555C1HR80BB01D
11 | 2 | C22 C25 | 22nF, 50V, 10%, X7R, Ceramic, 0402 | Murata Electronics North America | GRM155R71H223KA12D | Digi-Key | 490-3884-1-ND | CAPC100X50X55L25N | -55°C | 125°C | 2638 | GRM155R71H223KA12D
12 | 4 | C23 C24 C27 C28 | 12pF, 50V, 1%, NP0, Ceramic, 0402 | Murata | GJM1555C1H120FB01D | Digi-Key | 490-11190-1-ND | CAPC100X50X55L25N | -55°C | 125°C | 28705807 | GJM1555C1H120FB01D
13 | 2 | C26 C44 | 0.47uF, 25V, 10%, X5R, Ceramic, 0402 | TDK | C1005X5R1E474K050BB | Digi-Key | 445-8020-1-ND | CAPC100X50X55L15N | -55°C | 85°C | 522 | C1005X5R1E474K050BB
14 | 1 | C32 | 15nF, 100V, 10%, X7R, Ceramic, 0603 | Murata | GCM188R72A153KA37D | Digi-Key | 490-8029-1-ND | CAPC160X80X90L35N | -55°C | 125°C | 24561 | GCM188R72A153KA37D
15 | 3 | C41 C43 C56 | 1uF, 25V, 10%, X5R, Ceramic, 0603 | AVX | 06033D105KAT2A | Digi-Key | 478-5142-1-ND | CAPC1608X94N | -55°C | 85°C | 396328 | 06033D105KAT2A
16 | 2 | C45 C46 | 10nF, 50V, 10%, X8R, Ceramic, 0402 | TDK | C1005X8R1H103K050BB | Digi-Key | 445-8851-1-ND | CAPC100X50X55L15N | -55°C | 150°C | 2503 | C1005X8R1H103K050BB
17 | 2 | C47 C48 | 68nF, 50V, 5%, X7R, Ceramic, 0603 | Kemet | C0603C683J5RACTU | Digi-Key | 399-9121-1-ND | CAPC160X80X87L35N | -55°C | 125°C | 12690 | C0603C683J5RACTU
18 | 1 | C49 | 47nF, 50V, 10%, X7R, Ceramic, 0402 | TDK | CGA2B3X7R1H473K050BB | Digi-Key | 445-6897-1-ND | CAPC100X50X55L20N | -55°C | 125°C | 3520015 | CGA2B3X7R1H473K050BB
19 | 1 | C50 | 1.8nF, 50V, 10%, X7R, Ceramic, 0402 | AVX | 04025C182KAT2A | Digi-Key | 478-1104-1-ND | CAPC100X50X56L25N | -55°C | 125°C | 105451 | 04025C182KAT2A
20 | 1 | C51 | 100pF, 50V, 5%, C0G, Ceramic, 0603 | KEMET | C0603T101J5GCLTU | Digi-Key | 399-6300-1-ND | CAPC160X80X87L35N | -55°C | 125°C | 6469 | C0603T101J5GCLTU
21 | 1 | C52 | 0.1uF, 50V, 10%, X7R, Ceramic, 0603 | AVX | 06035C104KAZ2A | Digi-Key | 478-3540-1-ND | CAPC1608X94N | -55°C | 125°C | 2267120 | 06035C104KAZ2A
22 | 2 | C53 C54 | 10uF, 35V, 20%, X5R, Ceramic, 0603 | Murata | GRM188R6YA106MA73D | Digi-Key | 490-13248-1-ND | CAPC160X80X100L37N | -55°C | 85°C | 799215 | GRM188R6YA106MA73D
23 | 1 | C57 | 100pF, 50V, 1%, C0G, Ceramic, 0402 | AVX | 04025A101FAT2A | Digi-Key | 478-3658-1-ND | CAPC100X50X56L25N | -55°C | 125°C | 353589 | 04025A101FAT2A
24 | 1 | D1 | LED, Green, 2.1V, 20mA | SunLED | XZVG54W-8 | Digi-Key | 1497-1434-1-ND | LEDC200X125X120L40N | -40°C | 85°C | 12030 | XZVG54W-8
25 | 1 | D2 | LED Red/Yel, 2.2V/2V, 20mA, 1206 | SunLED | XZM2CRKCYK55W-8 | Digi-Key | 1497-1306-1-ND | SUNLED_XZM2CRKCYK55W-8 | -40°C | 85°C | 6541 | XZM2CRKCYK55W-8
26 | 1 | D3 | LED, Green, 2.1V, 10mA, 3.2mcd, 0603 | Lite-On Inc. | LTST-C190GKT | Digi-Key | 160-1183-1-ND | LEDC1608X80N | -55°C | 85°C | 790591 | LTST-C190GKT
27 | 1 | F1 | Fuse, 2A, 63VDC, Slow, 1206 | Bourns | SF-1206SP200M-2 | Digi-Key | SF-1206SP200M-2CT-ND | FUSC320X160X117L51N | -55°C | 150°C | 3630 | SF-1206SP200M-2
28 | 1 | J1 | FFC/FPC, 6pos, 0.5mm, 0.5A, 50V, R/A, SMD | Molex | 5034800600 | Digi-Key | WM1387CT-ND | Molex_503480-0600 | -40°C | 85°C | 47873 | 503480-0600
29 | 1 | L1 | 3.9nH, 400mA, High Frequency, 0402 | TDK | MLK1005S3N9ST000 | Digi-Key | 445-1462-1-ND | INDC1005X60L15 | -55°C | 125°C | 41815 | MLK1005S3N9ST000
30 | 1 | L2 | 10uH, 100mA, Wirewound, 0603 | Abracon | AISC-0603F-100J-T | Digi-Key | 535-12537-1-ND | Abracon_AISC-0603F | -40°C | 85°C | 5900 | AISC-0603F-100J-T
31 | 1 | L3 | 15nH, 300mA, High Frequency, 0402 | TDK | MLK1005S15NJT000 | Digi-Key | 445-1469-1-ND | INDC1005X60L15 | -55°C | 125°C | 42575 | MLK1005S15NJT000
32 | 1 | Q2 | MOSFET, P-CH, 20V, 3.6A, SOT-23 | Diodes | DMP2035U-7 | Digi-Key | DMP2035U-7DICT-ND | SOT23-3P91_240X120L53X44 | -55°C | 150°C | 0 | DMP2035U-7
33 | 1 | R1 | 100K, 1%, 50V, 1/16W, Thick, 0402 | Vishay | CRCW0402100KFKED | Digi-Key | 541-100KLCT-ND | RESC100X50X40L25 | -55°C | 155°C | 7 | CRCW0402100KFKED
34 | 1 | R2 | 4.99K, 1%, 50V, 1/16W, Thick, 0402 | Vishay | CRCW04024K99FKED | Digi-Key | 541-4.99KLCT-ND | RESC100X50X40L25 | -55°C | 155°C | 72 | CRCW04024K99FKED
35 | 1 | R4 | DNP, 4.99K, 1%, 50V, 1/16W, Thick, 0402 |  |  |  |  | RESC100X50X40L25 | -55°C | 155°C |  | _DNP
36 | 1 | R5 | 140 Ohms, 1%, 75V, 1/10W, Thick, 0603 | Vishay | CRCW0603140RFKEA | Digi-Key | 541-140HCT-ND | RESC155X85X50L30N | -55°C | 155°C | 0 | CRCW0603140RFKEA
37 | 4 | R7 R8 R9 R12 | 33 Ohms, 1%, 50V, 1/10W, Thick, 0402 | Panasonic | ERJ-2RKF33R0X | Digi-Key | P33.0LCT-ND | RESC100X50X40L25 | -55°C | 155°C | 4791611 | ERJ-2RKF33R0X
38 | 4 | R10 R19 R26 R33 | 10K, 1%, 50V, 1/10W, Thick, 0402 | Panasonic Electronic Components | ERJ-2RKF1002X | Digi-Key | P10.0KLCT-ND | RESC100X50X40L25 | -55°C | 155°C | 286646 | ERJ-2RKF1002X
39 | 4 | R11 R35 R36 R37 | 1M, 1%, 50V, 1/10W, Thick, 0402 | Panasonic | ERJ-2RKF1004X | Digi-Key | P1.00MLCT-ND | RESC100X50X40L25 | -55°C | 155°C | 814643 | ERJ-2RKF1004X
40 | 1 | R13 | DNP, Jumper, 50V, 1/16W, Thick, 0402 | Vishay | CRCW04020000Z0ED | Digi-Key | 541-0.0JCT-ND | RESC100X50X40L25 | -55°C | 155°C | 0 | DNP (CRCW04020000Z0ED)
41 | 1 | R14 | 10K, 1%, 50V, 1/16W, Thick, 0402 | Vishay | CRCW040210K0FKED | Digi-Key | 541-10.0KLCT-ND | RESC100X50X40L25 | -55°C | 155°C | 0 | CRCW040210K0FKED
42 | 1 | R15 | 357 Ohms, 1%, 75V, 1/10W, Thick, 0603 | Vishay | CRCW0603357RFKEA | Digi-Key | 541-357HCT-ND | RESC155X85X50L30N | -55°C | 155°C | 0 | CRCW0603357RFKEA
43 | 1 | R16 | 1.5K, 5%, 75V, 1/10W, Thick, 0603 | Vishay | CRCW06031K50JNEA | Digi-Key | 541-1.5KGCT-ND | RESC155X85X50L30N | -55°C | 155°C | 23788 | CRCW06031K50JNEA
44 | 2 | R17 R20 | 1M, 1%, 50V, 1/16W, Thick, 0402 | KOA Speer | RK73H1ETTP1004F | Mouser | 660-RK73H1ETTP1004F | RESC1005X40N | -55°C | 155°C | 0 | RK73H1ETTP1004F
45 | 3 | R22 R34 R39 | 100 Ohms, 1%, 50V, 1/10W, Thick, 0402 | Panasonic | ERJ-2RKF1000X | Digi-Key | P100LCT-ND | RESC100X50X40L25 | -55°C | 155°C | 0 | ERJ-2RKF1000X
46 | 1 | R30 | 140K, 1%, 50V, 1/10W, Thick, 0402 | Panasonic | ERJ-2RKF1403X | Digi-Key | P140KLCT-ND | RESC100X50X40L25 | -55°C | 155°C | 8517 | ERJ-2RKF1403X
47 | 1 | R31 | 100K, 1%, 50V, 1/10W, Thick, 0402 | Panasonic | ERJ-2RKF1003X | Digi-Key | P100KLCT-ND | RESC100X50X40L25 | -55°C | 155°C | 3554981 | ERJ-2RKF1003X
48 | 1 | R38 | DNP, 100K, 1%, 150V, 1/8W, Thick, 0805 | Vishay | DNP(CRCW0805100KFKEA) |  |  | RESC205X125X50L35N | -55°C | 155°C |  | DNP (CRCW0805100KFKEA)
49 | 2 | R44 R45 | 4.02K, 1%, 50V, 1/10W, Thick, 0402 | Panasonic | ERJ-2RKF4021X | Digi-Key | P4.02KLCT-ND | RESC100X50X40L25 | -55°C | 155°C | 8861 | ERJ-2RKF4021X
50 | 1 | R51 | Jumper, 50V, 1/16W, Thick, 0402 | Vishay | CRCW04020000Z0ED | Digi-Key | 541-0.0JCT-ND | RESC100X50X40L25 | -55°C | 155°C | 0 | CRCW04020000Z0ED
51 | 1 | RT2 | Thermistor, NTC, 10K, Max Temp 125°C,TH | Cantherm | MF52A2103J3470 | Digi-Key | 317-1258-ND | THRMRB220W45L300T300H950 | -55°C | 125°C | 5816 | MF52A2103J3470
52 | 1 | SW1 | Switch, Reed, SPST-NO, 100mA, 30V, SM | Standex | MK24-A-3 | Digi-Key | 374-1138-1-ND | standex_mk24-a-3 | -40°C | 115°C | 25157 | MK24-A-3
53 | 12 | TP7 TP8 TP9 TP12 TP19 TP20 TP21 TP23 TP24 TP25 TP26 TP27 | DNP, Test Point, SMD, 25 mil Round Pad | NA | NA | NA | NA | TP_C0635 | NA | NA |  | TP_C065
54 | 2 | TP28 TP29 | Test Point, Miniature, 3.4mm x 1.8mm Pad, SMD | Keystone | 5015 | Digi-Key | 36-5015CT-ND | TP340X180N |  |  | 7007618 | 5015
55 | 1 | U1 | Temperature, Digital, -40~125°C, 6WDFN | TI | TMP117AIDRVR | Digi-Key | 296-51834-1-ND | son7p65_200x200x80l25x30t160x100n | -55°C | 150°C | 0 | TMP117AIDRVR
56 | 1 | U10 | Buffer, Triple, Open Drain, 8XSON | Nexperia USA Inc. | 74LVC3G07GS,115 | Digi-Key | 1727-8082-1-ND | PSON8P35_135X100X35L31X16N | -40°C | 125°C | 5946 | 74LVC3G07GS,115
57 | 1 | U2 | Pressure Sensor, 0 ~30bar, ±400 mbar, I2C, SMD | TE Connectivity Measurement Specialties | MS583730BA01-50 | Digi-Key | 223-1704-1-ND | icdfn4_330x330x285l130x130 | -20°C | 85°C | 6794 | MS583730BA01-50
58 | 1 | U3 | Buffer, Single, Open Drain, 6-SON | TI | SN74LVC1G07QDRYRQ1 | Digi-Key | 296-SN74LVC1G07QDRYRQ1CT-ND | pson6p50_145x100x55l30x20n | -40°C | 125°C | 4 | SN74LVC1G07QDRYRQ1
59 | 1 | U5 | SOC, 2.4 GHz Bluetooth, Cortex M4 MCU, 512K Flash, 64K RAM, 48QFN | Nordic | NRF52832-QFAA-R | Digi-Key | 1490-1052-1-ND | QFN40P600X600X90-49N | -40°C | 85°C | 0 | nRF52832-QFAA-R
60 | 1 | U6 | Flash Memory, 16Mbit, 80MHz, 8USON | Macronix | MX25R1635FZUIH0 | Digi-Key | 1092-1178-1-ND | PSON9P50_200X300X60L40X25T160X20N | -40°C | 85°C | 32590 | MX25R1635FZUIH0
61 | 1 | U7 | Battery Charger, Multi-Chemistry, 60V, 250mA, 10DFN | Analog Devices Inc. | LTC4079EDD#TRPBF | Digi-Key | LTC4079EDD#TRPBFCT-ND | SON11P50_300X300X80L40X25T238X165N | -40°C | 125°C | 0 | LTC4079EDD#TRPBF
62 | 1 | U8 | Wireless Power Supply Receiver, 20QFN | Texas Instruments | BQ51013ARHLR | Digi-Key | 296-30568-1-ND | QFN50P450X350X100-21N | 0°C | 125°C | 0 | BQ51013ARHLR
63 | 1 | U9 | Opamp, Single, GP, RRIO, 6.2kHz, SC70-5 | Texas Instruments | LPV521MG/NOPB | Digi-Key | 296-39069-1-ND | SOT23-5P65_210X110L36X22N | -40°C | 125°C | 0 | LPV521MG/NOPB
64 | 1 | Y2 | Crystal, 32MHz, 8pF, SMD | ECS | ECS-320-8-37CKM | Digi-Key | XC1547CT-ND | OSCCC200X160X46-4NA | -20°C | 70°C | 700896 | ECS-320-8-37CKM
65 | 1 | Y4 | Crystal, 32.768kHz, 9pF, SMD | Abracon | ABS05-32.768KHZ-9-T | Digi-Key | 535-11897-1-ND | DFN160X100X50-2NA | -40°C | 85°C | 1041278 | ABS05-32.768KHZ-9-T
66 | 1 | L4 | Coil | TDK | WR303050-15F5-G | Digi-Key | 445-16092-ND | N/A

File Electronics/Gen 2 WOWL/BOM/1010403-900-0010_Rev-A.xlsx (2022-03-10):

WOWL Board Assembly/BOM |  |  |  |  |  | Part Supplied by Creare
Project: | 1010403 Gone Fishing |  |  |  |  | DNP = Do Not Populate
Part #: | 1010403-900-0010 |  | Released 02/22/2022 RWM
Revision: | A
Item | Quantity | Reference | Description | Manufacturer | Manufacturer Part# | Suggested Vendor | Suggested Vendor Part # | Footprint | Temp Min | Temp Max
1 | 1 | DOC | Schematic | Creare | 1010403-900-0011, Rev.A | N/A | N/A | N/A | N/A | N/A
2 | 1 | PCB | PCB |  | 1010403-900-0012, Rev.A | N/A | N/A | N/A | N/A | N/A
3 | 1 | ANT1 | PCB Antenna, 2.4GHz | DNP | DNP | DNP | DNP | pcbantenna_an043 | - | - |  | TMP-5069
4 | 2 | B1 B2 | BATTERY NIMH 1.2V 700MAH AAA | Panasonic - BSG | HHR70AAAB8T | Digi-Key | P213T-ND | PANASONIC_HHR70AAAB8T | -10°C | 65°C | 37 | HHR70AAAB8T
5 | 15 | C1 C3 C4 C5 C7 C8 C10 C12 C13 C14 C15 C40 C42 C43 C55 | 0.1uF, 50V, 10%, X7R, Ceramic, 0402 | TDK | CGA2B3X7R1H104K050BB | Digi-Key | 445-6899-1-ND | CAPC100X50X55L20N | -55°C | 125°C | 0 | CGA2B3X7R1H104K050BB
6 | 1 | C2 | 10uF, 10V, 20%, X5R, Ceramic, 0402 | Samsung | CL05A106MP8NUB8 | Digi-Key | 1276-6830-1-ND | CAPC100X50X90L25N | -55°C | 85°C | 5063507 | CL05A106MP8NUB8
7 | 1 | C11 | DNP 10uF, 10V, 20%, X5R, Ceramic, 0402 | Samsung | CL05A106MP8NUB8 | Digi-Key | 1276-6830-1-ND | CAPC100X50X90L25N | -55°C | 85°C | 5063507 | CL05A106MP8NUB8
8 | 1 | C6 | 4.7uF, 10V, 10%, X5R, Ceramic, 0402 | Murata | ZRB15XR61A475KE01D | Digi-Key | 490-13252-1-ND | CAPC100X50X80L25N | -55°C | 85°C | 0 | ZRB15XR61A475KE01D
9 | 1 | C9 | 4.7uF, 10V, 10%, X5R, Ceramic, 0402 | TDK | C1005X5R1A475K050BC | Digi-Key | 445-13820-1-ND | CAPC102X52X65L15N | -55°C | 85°C | 219784 | C1005X5R1A475K050BC
10 | 1 | C16 | 3.4pF, 50V, ±0.1pF, C0G, Ceramic, 0402 | KEMET | CBR04C349B5GAC | Digi-Key | 399-16077-1-ND | CAPC100X50X55L22N | -55°C | 125°C | 10161 | CBR04C349B5GAC
11 | 1 | C17 | 0.22uF, 35V, 10%, X7R, Ceramic, 0402 | TDK | C1005X7R1V224K050BE | Digi-Key | 445-173778-1-ND | CAPC100X50X60L15N | -55°C | 125°C | 131145 | C1005X7R1V224K050BE
12 | 1 | C18 | 1.2PF, 50V, ±0.05pF, C0G, Ceramic, 0402 | Murata | GJM1555C1H1R2WB01D | Digi-Key | 490-11195-1-ND | CAPC100X50X55L25N | -55°C | 125°C | 85355 | GJM1555C1H1R2WB01D
13 | 1 | C19 | 0.5pF, 50V, ±0.1pF, C0G, Ceramic, 0402 | Murata | GJM1555C1HR50BB01D | Digi-Key | 490-6077-1-ND | CAPC100X50X55L25N | -55°C | 125°C | 205830 | GJM1555C1HR50BB01D
14 | 2 | C20 C21 | DNP, 1uF, 10V, 10%, X7S, Ceramic, 0402 | TDK | C1005X7S1A105K050BC | Digi-Key | 445-9116-1-ND | CAPC100X50X55L15N | -55°C | 125°C | 0 | DNP (C1005X7S1A105K050BC)
15 | 2 | C22 C25 | 22nF, 50V, 10%, X7R, Ceramic, 0402 | Murata Electronics North America | GRM155R71H223KA12D | Digi-Key | 490-3884-1-ND | CAPC100X50X55L25N | -55°C | 125°C | 164098 | GRM155R71H223KA12D
16 | 2 | C23 C24 | DNP 12pF, 50V, 1%, NP0, Ceramic, 0402 | Murata | GJM1555C1H120FB01D | Digi-Key | 490-11190-1-ND | CAPC100X50X55L25N | -55°C | 125°C | 29087109 | GJM1555C1H120FB01D
17 | 2 | C27 C28 | 12pF, 50V, 1%, NP0, Ceramic, 0402 | Murata | GJM1555C1H120FB01D | Digi-Key | 490-11190-1-ND | CAPC100X50X55L25N | -55°C | 125°C | 29087109 | GJM1555C1H120FB01D
18 | 2 | C26 C44 | 0.47uF, 25V, 10%, X5R, Ceramic, 0402 | TDK | C1005X5R1E474K050BB | Digi-Key | 445-8020-1-ND | CAPC100X50X55L15N | -55°C | 85°C | 74416 | C1005X5R1E474K050BB
19 | 1 | C32 | 15nF, 100V, 10%, X7R, Ceramic, 0603 | Murata | GCM188R72A153KA37D | Digi-Key | 490-8029-1-ND | CAPC160X80X90L35N | -55°C | 125°C | 42525 | GCM188R72A153KA37D
20 | 1 | C41 | 1uF, 25V, 10%, X5R, Ceramic, 0603 | AVX Corporation | 06033D105KAT2A | Digi-Key | 478-5142-1-ND | CAPC1608X94N | -55°C | 85°C | 0 | 06033D105KAT2A
21 | 2 | C45 C46 | 10nF, 50V, 10%, X8R, Ceramic, 0402 | TDK Corporation | C1005X8R1H103K050BB | Digi-Key | 445-8851-1-ND | CAPC100X50X55L15N | -55°C | 150°C | 29507 | C1005X8R1H103K050BB
22 | 2 | C47 C48 | 68nF, 50V, 5%, X7R, Ceramic, 0603 | Kemet | C0603C683J5RACTU | Digi-Key | 399-9121-1-ND | CAPC160X80X87L35N | -55°C | 125°C | 10196 | C0603C683J5RACTU
23 | 1 | C49 | 47nF, 50V, 10%, X7R, Ceramic, 0402 | TDK | CGA2B3X7R1H473K050BB | Digi-Key | 445-6897-1-ND | CAPC100X50X55L20N | -55°C | 125°C | 1189265 | CGA2B3X7R1H473K050BB
24 | 1 | C50 | 1.8nF, 50V, 10%, X7R, Ceramic, 0402 | AVX | 04025C182KAT2A | Digi-Key | 478-1104-1-ND | CAPC100X50X56L25N | -55°C | 125°C | 28623 | 04025C182KAT2A
25 | 1 | C51 | 100pF, 50V, 5%, C0G, Ceramic, 0603 | KEMET | C0603T101J5GCLTU | Digi-Key | 399-6300-1-ND | CAPC160X80X87L35N | -55°C | 125°C | 3347 | C0603T101J5GCLTU
26 | 1 | C52 | 0.1uF, 50V, 10%, X7R, Ceramic, 0603 | AVX | 06035C104KAZ2A | Digi-Key | 478-3540-1-ND | CAPC1608X94N | -55°C | 125°C | 280629 | 06035C104KAZ2A
27 | 2 | C53 C54 | 10uF, 35V, 20%, X5R, Ceramic, 0603 | Murata | GRM188R6YA106MA73D | Digi-Key | 490-13248-1-ND | CAPC160X80X100L37N | -55°C | 85°C | 0 | GRM188R6YA106MA73D
28 | 1 | D1 | LED, Green, 2.1V, 20mA | SunLED | XZVG54W-8 | Digi-Key | 1497-1434-1-ND | LEDC200X125X120L40N | -40°C | 85°C | 11945 | XZVG54W-8
29 | 1 | D2 | LED Red/Yel, 2.2V/2V, 20mA, 1206 | SunLED | XZM2CRKCYK55W-8 | Digi-Key | 1497-1306-1-ND | SUNLED_XZM2CRKCYK55W-8 | -40°C | 85°C | 6361 | XZM2CRKCYK55W-8
30 | 1 | D3 | LED, Green, 2.1V, 10mA, 3.2mcd, 0603 | Lite-On Inc. | LTST-C190GKT | Digi-Key | 160-1183-1-ND | LEDC1608X80N | -55°C | 85°C | 0 | LTST-C190GKT
31 | 1 | F1 | DNP Fuse, 2A, 63VDC, Slow, 1206 | Bourns | SF-1206SP200M-2 | Digi-Key | SF-1206SP200M-2CT-ND | FUSC320X160X117L51N | -55°C | 150°C | 36 | SF-1206SP200M-2
32 | 1 | J1 | FFC/FPC, 6pos, 0.5mm, 0.5A, 50V, R/A, SMD | Molex | 5034800600 | Digi-Key | WM1387CT-ND | Molex_503480-0600 | -40°C | 85°C | 12008 | 503480-0600
33 | 1 | L1 | 3.3nH, 2A, High Freq., Wirewound, 0402 | Murata | LQW15AN3N3B80D | Digi-Key | 490-7641-1-ND | INDC100X60X60L20N | -55°C | 125°C | 119782 | LQW15AN3N3B80D
34 | 1 | L2 | 22nH, 350mA, High Frequency, 0402 | Murata | LQG15HS22NH02D | Digi-Key | 490-15112-1-ND | INDC100X50X55L25N | -55°C | 125°C | 22432 | LQG15HS22NH02D
35 | 1 | L3 | 10uH, 200mA, 1.2 OHM, 0603 | KEMET | L0603B100KPWFT | Digi-Key | 399-17789-1-ND | indc160x80x90l35n | -40°C | 105°C | 732 | L0603B100KPWFT
36 | 1 | Q2 | MOSFET, P-CH, 20V, 3.6A, SOT-23 | Diodes | DMP2035U-7 | Digi-Key | DMP2035U-7DICT-ND | SOT23-3P91_240X120L53X44 | -55°C | 150°C | 0 | DMP2035U-7
37 | 1 | R1 | DNP, 100K, 1%, 150V, 1/8W, Thick, 0805 | Vishay | DNP(CRCW0805100KFKEA) |  |  | RESC205X125X50L35N | -55°C | 155°C |  | DNP (CRCW0805100KFKEA)
38 | 1 | R2 | 100K, 1%, 50V, 1/16W, Thick, 0402 | Vishay | CRCW0402100KFKED | Digi-Key | 541-100KLCT-ND | RESC100X50X40L25 | -55°C | 155°C | 0 | CRCW0402100KFKED
39 | 1 | R3 | 4.99K, 1%, 50V, 1/16W, Thick, 0402 | Vishay | CRCW04024K99FKED | Digi-Key | 541-4.99KLCT-ND | RESC100X50X40L25 | -55°C | 155°C | 0 | CRCW04024K99FKED
40 | 1 | R4 | 4.99K, 1%, 50V, 1/16W, Thick, 0402 | Vishay | CRCW04024K99FKED | Digi-Key | 541-4.99KLCT-ND | RESC100X50X40L25 | -55°C | 155°C | 0 | CRCW04024K99FKED
41 | 1 | R5 | 140 Ohms, 1%, 75V, 1/10W, Thick, 0603 | Vishay Dale | CRCW0603140RFKEA | Digi-Key | 541-140HCT-ND | RESC1609X50N | -55°C | 155°C | 0 | CRCW0603140RFKEA
42 | 1 | R6 | Jumper, 50V, 1.5A, Thick, 0402 | Stackpole | RMCF0402ZT0R00 | Digi-Key | RMCF0402ZT0R00CT-ND | RESC100X50X40L25 | -55°C | 155°C | 6040836 | RMCF0402ZT0R00
43 | 4 | R7 R8 R9 R12 | 33 Ohms, 1%, 50V, 1/10W, Thick, 0402 | Panasonic | ERJ-2RKF33R0X | Digi-Key | P33.0LCT-ND | RESC100X50X40L25 | -55°C | 155°C | 0 | ERJ-2RKF33R0X
44 | 4 | R10 R19 R26 R33 | 10K, 1%, 50V, 1/10W, Thick, 0402 | Panasonic Electronic Components | ERJ-2RKF1002X | Digi-Key | P10.0KLCT-ND | RESC100X50X40L25 | -55°C | 155°C | 0 | ERJ-2RKF1002X
45 | 4 | R11 R35 R36 R37 | 1M, 1%, 50V, 1/10W, Thick, 0402 | Panasonic | ERJ-2RKF1004X | Digi-Key | P1.00MLCT-ND | RESC100X50X40L25 | -55°C | 155°C | 0 | ERJ-2RKF1004X
46 | 1 | R13 | DNP, Jumper, 50V, 1/16W, Thick, 0402 | Vishay | CRCW04020000Z0ED | Digi-Key | 541-0.0JCT-ND | RESC100X50X40L25 | -55°C | 155°C | 0 | DNP (CRCW04020000Z0ED)
47 | 1 | R14 | 10K, 1%, 50V, 1/16W, Thick, 0402 | Vishay | CRCW040210K0FKED | Digi-Key | 541-10.0KLCT-ND | RESC100X50X40L25 | -55°C | 155°C | 0 | CRCW040210K0FKED
48 | 1 | R15 | 357 Ohms, 1%, 75V, 1/10W, Thick, 0603 | Vishay | CRCW0603357RFKEA | Digi-Key | 541-357HCT-ND | RESC155X85X50L30N | -55°C | 155°C | 0 | CRCW0603357RFKEA
49 | 1 | R16 | 1.5K, 5%, 75V, 1/10W, Thick, 0603 | Vishay Dale | CRCW06031K50JNEA | Digi-Key | 541-1.5KGCT-ND | RESC1609X50N | -55°C | 155°C | 0 | CRCW06031K50JNEA
50 | 2 | R17 R20 | 1M, 1%, 50V, 1/16W, Thick, 0402 | KOA Speer | RK73H1ETTP1004F | Mouser | 660-RK73H1ETTP1004F | RESC1005X40N | -55°C | 155°C | 0 | RK73H1ETTP1004F
51 | 3 | R22 R34 R39 | 100 Ohms, 1%, 50V, 1/10W, Thick, 0402 | Panasonic | ERJ-2RKF1000X | Digi-Key | P100LCT-ND | RESC100X50X40L25 | -55°C | 155°C | 0 | ERJ-2RKF1000X
52 | 1 | R30 | 140K, 1%, 50V, 1/10W, Thick, 0402 | Panasonic | ERJ-2RKF1403X | Digi-Key | P140KLCT-ND | RESC100X50X40L25 | -55°C | 155°C | 0 | ERJ-2RKF1403X
53 | 1 | R31 | 100K, 1%, 50V, 1/10W, Thick, 0402 | Panasonic | ERJ-2RKF1003X | Digi-Key | P100KLCT-ND | RESC100X50X40L25 | -55°C | 155°C | 0 | ERJ-2RKF1003X
54 | 2 | R44 R45 | 4.02K, 1%, 50V, 1/10W, Thick, 0402 | Panasonic | ERJ-2RKF4021X | Digi-Key | P4.02KLCT-ND | RESC100X50X40L25 | -55°C | 155°C | 0 | ERJ-2RKF4021X
55 | 1 | RT2 | Thermistor, NTC, 10K, Max Temp 125°C,TH | Cantherm | MF52A2103J3470 | Digi-Key | 317-1258-ND | THRMRB220W45L300T300H950 | -55°C | 125°C | 14068 | MF52A2103J3470
56 | 1 | SW1 | Switch, Reed, SPST-NO, 100mA, 30V, SM | Standex | MK24-A-3 | Digi-Key | 374-1138-1-ND | standex_mk24-a-3 | -40°C | 115°C | 28380 | MK24-A-3
57 | 12 | TP1 TP2 TP3 TP7 TP8 TP9 TP10 TP11 TP12 TP23 TP24 TP27 | DNP, Test Point, SMD, 25 mil Round Pad | NA | NA | NA | NA | TP_C0635 |  |  |  | TP_C065
58 | 2 | TP28 TP29 | Test Point, Miniature, 3.4mm x 1.8mm Pad, SMD | Keystone | 5015 | Digi-Key | 36-5015CT-ND | TP340X180N |  |  | 1053555 | 5015
59 | 1 | U1 | Temperature, Digital, -40~125°C, 6WDFN | TI | TMP117AIDRVR | Digi-Key | 296-51834-1-ND | son7p65_200x200x80l25x30t160x100n | -55°C | 150°C | 7323 | TMP117AIDRVR
60 | 1 | U10 | Buffer, Triple, Open Drain, 8XSON | Nexperia USA Inc. | 74LVC3G07GS,115 | Digi-Key | 1727-8082-1-ND | PSON8P35_135X100X35L31X16N | -40°C | 125°C | 6854 | 74LVC3G07GS,115
61 | 1 | U2 | Pressure Sensor, 0 ~30bar, ±400 mbar, I2C, SMD | TE Connectivity Measurement Specialties | MS583730BA01-50 | Digi-Key | 223-1704-1-ND | icdfn4_330x330x285l130x130 | -20°C | 85°C | 2800 | MS583730BA01-50
62 | 1 | U3 | RF Filter, Low Pass, 2.45GHZ Center, 4SMD | TDK | DLF162500LT-5028A1 | Digi-Key | 445-15658-1-ND | tdk_dlf162500lt-5028a1 | -40°C | 85°C | 38560 | DLF162500LT-5028A1
63 | 1 | U4 | IC BUFFER NON-INVERT 5.5V 6USON | TI | SN74LVC1G07QDRYRQ1 | Digi-Key | 296-SN74LVC1G07QDRYRQ1CT-ND | pson6p50_145x100x55l30x20n |  | -40C ~ 125C (TA) | 3950 | SN74LVC1G07QDRYRQ1
64 | 1 | U5 | SOC, 2.4 GHz Bluetooth, Cortex-M0+ MCU, 256K Flash, 64K RAM, 48QFN | STMicro | BLUENRG-355MT | Mouser | 511-BLUENRG-355MT | QFN49P40_600X600X105L40X21T450N | -40°C | 105°C | 0 | BLUENRG-355MT
65 | 1 | U6 | Flash Memory, 16Mbit, 80MHz, 8USON | Macronix | MX25R1635FZUIH0 | Digi-Key | 1092-1178-1-ND | PSON9P50_200X300X60L40X25T160X20N | -40°C | 85°C | 11460 | MX25R1635FZUIH0
66 | 1 | U7 | Battery Charger, Multi-Chemistry, 60V, 250mA, 10DFN | Analog Devices Inc. | LTC4079EDD#TRPBF | Digi-Key | LTC4079EDD#TRPBFCT-ND | SON11P50_300X300X80L40X25T238X165N | -40°C | 125°C | 9077 | LTC4079EDD#TRPBF
67 | 1 | U8 | Wireless Power Supply Receiver, 20QFN | Texas Instruments | BQ51013ARHLR | Digi-Key | 296-30568-1-ND | QFN50P450X350X100-21N | 0°C | 125°C | 144 | BQ51013ARHLR
68 | 1 | U9 | Opamp, Single, GP, RRIO, 6.2kHz, SC70-5 | Texas Instruments | LPV521MG/NOPB | Digi-Key | 296-39069-1-ND | SOT23-5P65_210X110L36X22N | -40°C | 125°C | 19940 | LPV521MG/NOPB
69 | 1 | Y2 | Crystal, 32MHz, 8pF, SMD | ECS | ECS-320-8-37CKM | Digi-Key | XC1547CT-ND | OSCCC200X160X46-4NA | -20°C | 70°C | 947 | ECS-320-8-37CKM
70 | 1 | Y4 | Crystal, 32.768kHz, 9pF, SMD | Abracon | ABS05-32.768KHZ-9-T | Digi-Key | 535-11897-1-ND | DFN160X100X50-2NA | -40°C | 85°C | 0 | ABS05-32.768KHZ-9-T
71 | 1 | L4 | Coil | TDK | WR303050-15F5-G | Digi-Key | 445-16092-ND | N/A

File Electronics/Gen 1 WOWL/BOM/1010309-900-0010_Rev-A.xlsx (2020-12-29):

WOWL Board Assembly/BOM |  |  |  |  |  | Part Supplied by Creare
Project: | 1010309 Gone Fishing |  |  |  |  | DNP = Do Not Populate
Part #: | 1010309-900-0010 |  | Released 8/31/2020 RMP
Revision: | A
Item | Quantity | Reference | Description | Manufacturer | Manufacturer Part# | Suggested Vendor | Suggested Vendor Part # | Footprint | Temp Min | Temp Max
1 | 1 | DOC | Schematic | Creare | 1010309-900-0011, Rev.A | N/A | N/A | N/A | N/A | N/A
2 | 1 | PCB | PCB |  | 1010309-900-0012, Rev.A | N/A | N/A | N/A | N/A | N/A
3 | 1 | ANT1 | PCB Antenna, 2.4GHz | DNP | DNP | DNP | DNP | pcbantenna_an043 | DNP | DNP
4 | 2 | B1,B2 | BATTERY NIMH 1.2V 700MAH AAA | Panasonic - BSG | HHR70AAAB8T | Digi-Key | P213T-ND | PANASONIC_HHR70AAAB8T | 65°C | -10°C
5 | 4 | C1,C7,C9,C17 | 1.5nF, 100V, 5%, C0G, Ceramic, 0603 | Murata | GCM1885C2A152JA16D | Digi-Key | 490-4951-1-ND | CAPC160X80X90L35N | 125°C | -55°C
6 | 16 | C2,C3,C4,C6,C8,C10,C11,C14,C15,C18,C20,C21,C30,C40,C42,C43 | 0.1uF, 50V, 10%, X7R, Ceramic, 0402 | TDK | CGA2B3X7R1H104K050BB | Digi-Key | 445-6899-1-ND | CAPC100X50X55L20N | 125°C | -55°C
7 | 3 | C5,C13,C32 | 15nF, 100V, 10%, X7R, Ceramic, 0603 | Murata | GCM188R72A153KA37D | Digi-Key | 490-8029-1-ND | CAPC160X80X90L35N | 125°C | -55°C
8 | 6 | C12,C31,C36,C37,C38,C39 | 22uF, 25V, 20%, X5R, Ceramic, 0805 | TDK Corporation | C2012X5R1E226M125AC | Digi-Key | 445-9112-1-ND | CAPC2013X145N | 85°C | -55°C
9 | 2 | C16,C22 | DNP, Capacitor, 0402 | NA | NA | DNP | DNP | CAPC1005X55L25N
10 | 1 | C19 | 0.8pF, 50V, ±0.1pF, NP0, Ceramic, 0402 | Murata | GJM1555C1HR80BB01D | Digi-Key | 490-6080-1-ND | CAPC100X50X55L25N | 125°C | -55°C
11 | 4 | C23,C24,C27,C28 | 12pF, 50V, 1%, NP0, Ceramic, 0402 | Kemet | C0402C120F5GACTU | Mouser | 80-C0402C120F5GACTU | CAPC100X50X55L25N | 125°C | -55°C
12 | 1 | C25 | 100pF, 50V, 1%, C0G, Ceramic, 0402 | AVX | 04025A101FAT2A | Digi-Key | 478-3658-1-ND | CAPC100X50X56L25N | 125°C | -55°C
13 | 2 | C26,C41 | 1uF, 25V, 10%, X5R, Ceramic, 0603 | AVX Corporation | 06033D105KAT2A | Digi-Key | 478-5142-1-ND | CAPC1608X94N | 85°C | -55°C
14 | 1 | C29 | 10nF, 50V, 5%, X7R, Ceramic, 0603 | Kemet | C0603C103J5RACTU | Digi-Key | 399-1092-1-ND | CAPC160X80X87L35N | 125°C | -55°C
15 | 2 | C33,C34 | 1nF, 50V, 1%, C0G, Ceramic, 0402 | Murata | GRM1555C1H102FA01D | Digi-Key | 490-6189-1-ND | CAPC100X50X55L25N | 125°C | -55°C
16 | 1 | C35 | 47nF, 50V, 10%, X7R, Ceramic, 0402 | TDK | CGA2B3X7R1H473K050BB | Digi-Key | 445-6897-1-ND | CAPC100X50X55L20N | 125°C | -55°C
17 | 1 | D1 | LED, Green, 2.1V, 20mA | SunLED | XZVG54W-8 | Digi-Key | 1497-1434-1-ND | LEDC200X125X120L40N | 85°C | -40°C
18 | 1 | D2 | LED Red/Yel, 2.2V/2V, 20mA, 1206 | SunLED | XZM2CRKCYK55W-8 | Digi-Key | 1497-1306-1-ND | SUNLED_XZM2CRKCYK55W-8 | 85°C | -40°C
19 | 1 | F1 | Fuse, 2A, 63VDC, Slow, 1206 | Bourns | SF-1206SP200M-2 | DNP | DNP | DNP | DNP | DNP
20 | 1 | J1 | FFC/FPC, 6pos, 0.5mm, 0.5A, 50V, R/A, SMD | Molex | 5034800600 | Digi-Key | WM1387CT-ND | Molex_503480-0600 | 85°C | -40°C
21 | 1 | L1 | 3.9nH, 400mA, High Frequency, 0402 | TDK | MLK1005S3N9ST000 | Digi-Key | 445-1462-1-ND | INDC1005X60L15 | 125°C | -55°C
22 | 1 | L2 | 10uH, 100mA, Wirewound, 0603 | Abracon | AISC-0603F-100J-T | Digi-Key | 535-12537-1-ND | Abracon_AISC-0603F | 85°C | -40°C
23 | 1 | L3 | 15nH, 300mA, High Frequency, 0402 | TDK Corporation | MLK1005S15NJT000 | Digi-Key | 445-1469-1-ND | INDC1005X60L15 | 125°C | -55°C
24 | 1 | L4 | 4.7uH, 700mA, Wirewound, 1210 | EPCOS (TDK) | B82422H1472K | Digi-Key | 495-2649-1-ND | INDM3225X240N | 150°C | -55°C
25 | 1 | Q2 | MOSFET, P-CH, 20V, 3.6A, SOT-23 | Diodes | DMP2035U-7 | Digi-Key | DMP2035U-7DICT-ND | SOT23-3P91_240X120L53X44 | 150°C | -55°C
26 | 14 | R1,R2,R3,R4,R6,R7,R8,R9,R12,R13,R14,R15,R16,R18 | 33 Ohms, 1%, 50V, 1/10W, Thick, 0402 | Panasonic | ERJ-2RKF33R0X | Digi-Key | P33.0LCT-ND | RESC100X50X40L25 | 155°C | -55°C
27 | 6 | R5,R11,R17,R35,R36,R37 | 1M, 1%, 50V, 1/10W, Thick, 0402 | Panasonic | ERJ-2RKF1004X | Digi-Key | P1.00MLCT-ND | RESC100X50X40L25 | 155°C | -55°C
28 | 10 | R10,R19,R20,R26,R27,R28,R29,R32,R33,R38 | 10K, 1%, 50V, 1/10W, Thick, 0402 | Panasonic Electronic Components | ERJ-2RKF1002X | Digi-Key | P10.0KLCT-ND | RESC100X50X40L25 | 155°C | -55°C
29 | 8 | R21,R22,R23,R34,R39,R43,R46,R50 | 100 Ohms, 1%, 50V, 1/10W, Thick, 0402 | Panasonic | ERJ-2RKF1000X | Digi-Key | P100LCT-ND | RESC100X50X40L25 | 155°C | -55°C
30 | 2 | R24,R25 | 12K, 0.1%, 150V, 1/4W, Thick, 0805 | Panasonic | ERJ-PB6B1202V | Digi-Key | P20716CT-ND | RESC200X125X70L40N | 155°C | -55°C
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

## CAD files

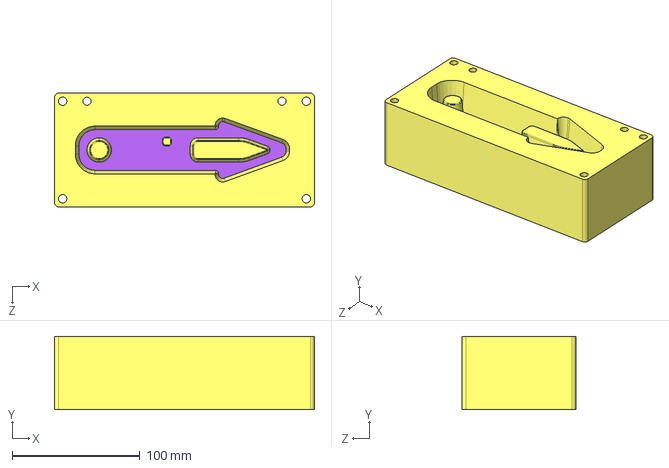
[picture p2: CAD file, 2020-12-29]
Encapsulation/Gen 1/WOWL Mold.STEP
203.2 x 57.2 x 88.9 mm
WOWL Mold KO 1
WOWL Mold Outer 1

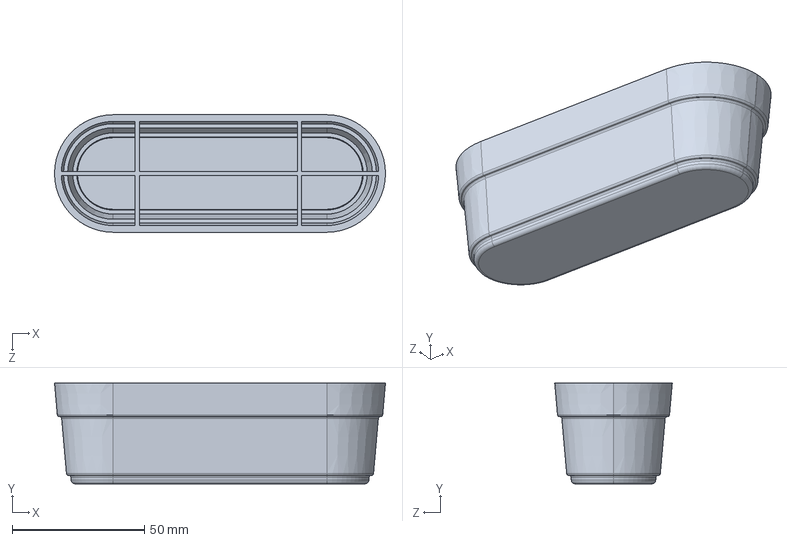
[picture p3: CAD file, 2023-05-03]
Encapsulation/Gen 3/Vacuum_Mold_Positive.STEP
125.3 x 38.1 x 44.5 mm

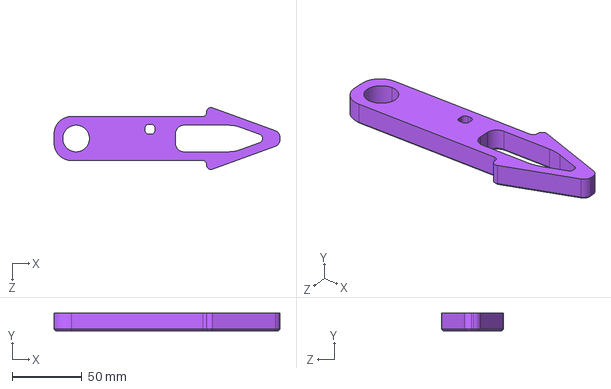
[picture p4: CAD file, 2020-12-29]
Encapsulation/Gen 1/WOWL Mold KO.STEP
161.9 x 12.7 x 44.4 mm

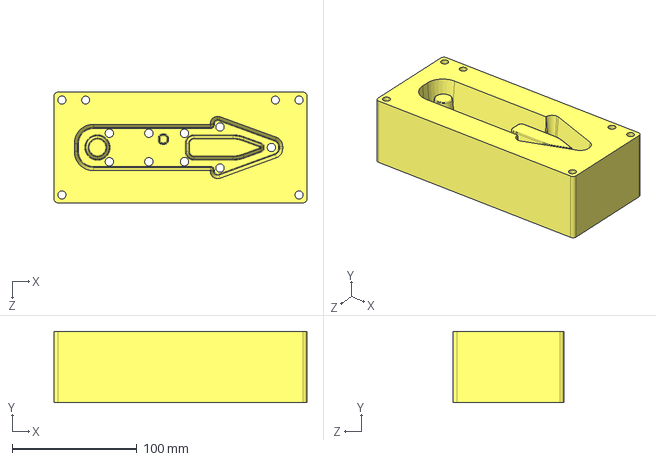
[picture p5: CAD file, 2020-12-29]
Encapsulation/Gen 1/WOWL Mold Outer.STEP
203.2 x 57.2 x 88.9 mm

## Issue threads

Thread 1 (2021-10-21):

### ISSUE TITLE
Day on Lobster Boat

### ISSUE THREAD

**Issue by EricDesjardins** [Open-Water-Logger/WOWL#1]
Details for our trip to Harpswell ME on 10/7/21:

Meeting with Dana (207-210-0015) @ 6AM at the Interstate Lobster Dock

Need to wear: Warm, wind-proof layers and muck boots

Need to bring: 
- Notebook and pen
- Stopwatch
- Waterproof phone case
- Disc golf bags (just in case)
- Cooler (for lobsters, hopefully)
- Raincoat
- Warm hat
- Sunglasses
- Waterproof Camera
- Lunch and Drink
- Gift for Dana

**Comment by dsully-dev** [comment]
I'll edit your list if I think of anything else. Thanks @EricDesjardins!

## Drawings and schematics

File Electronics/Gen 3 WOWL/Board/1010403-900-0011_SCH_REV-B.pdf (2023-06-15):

## Pressure

## JTag

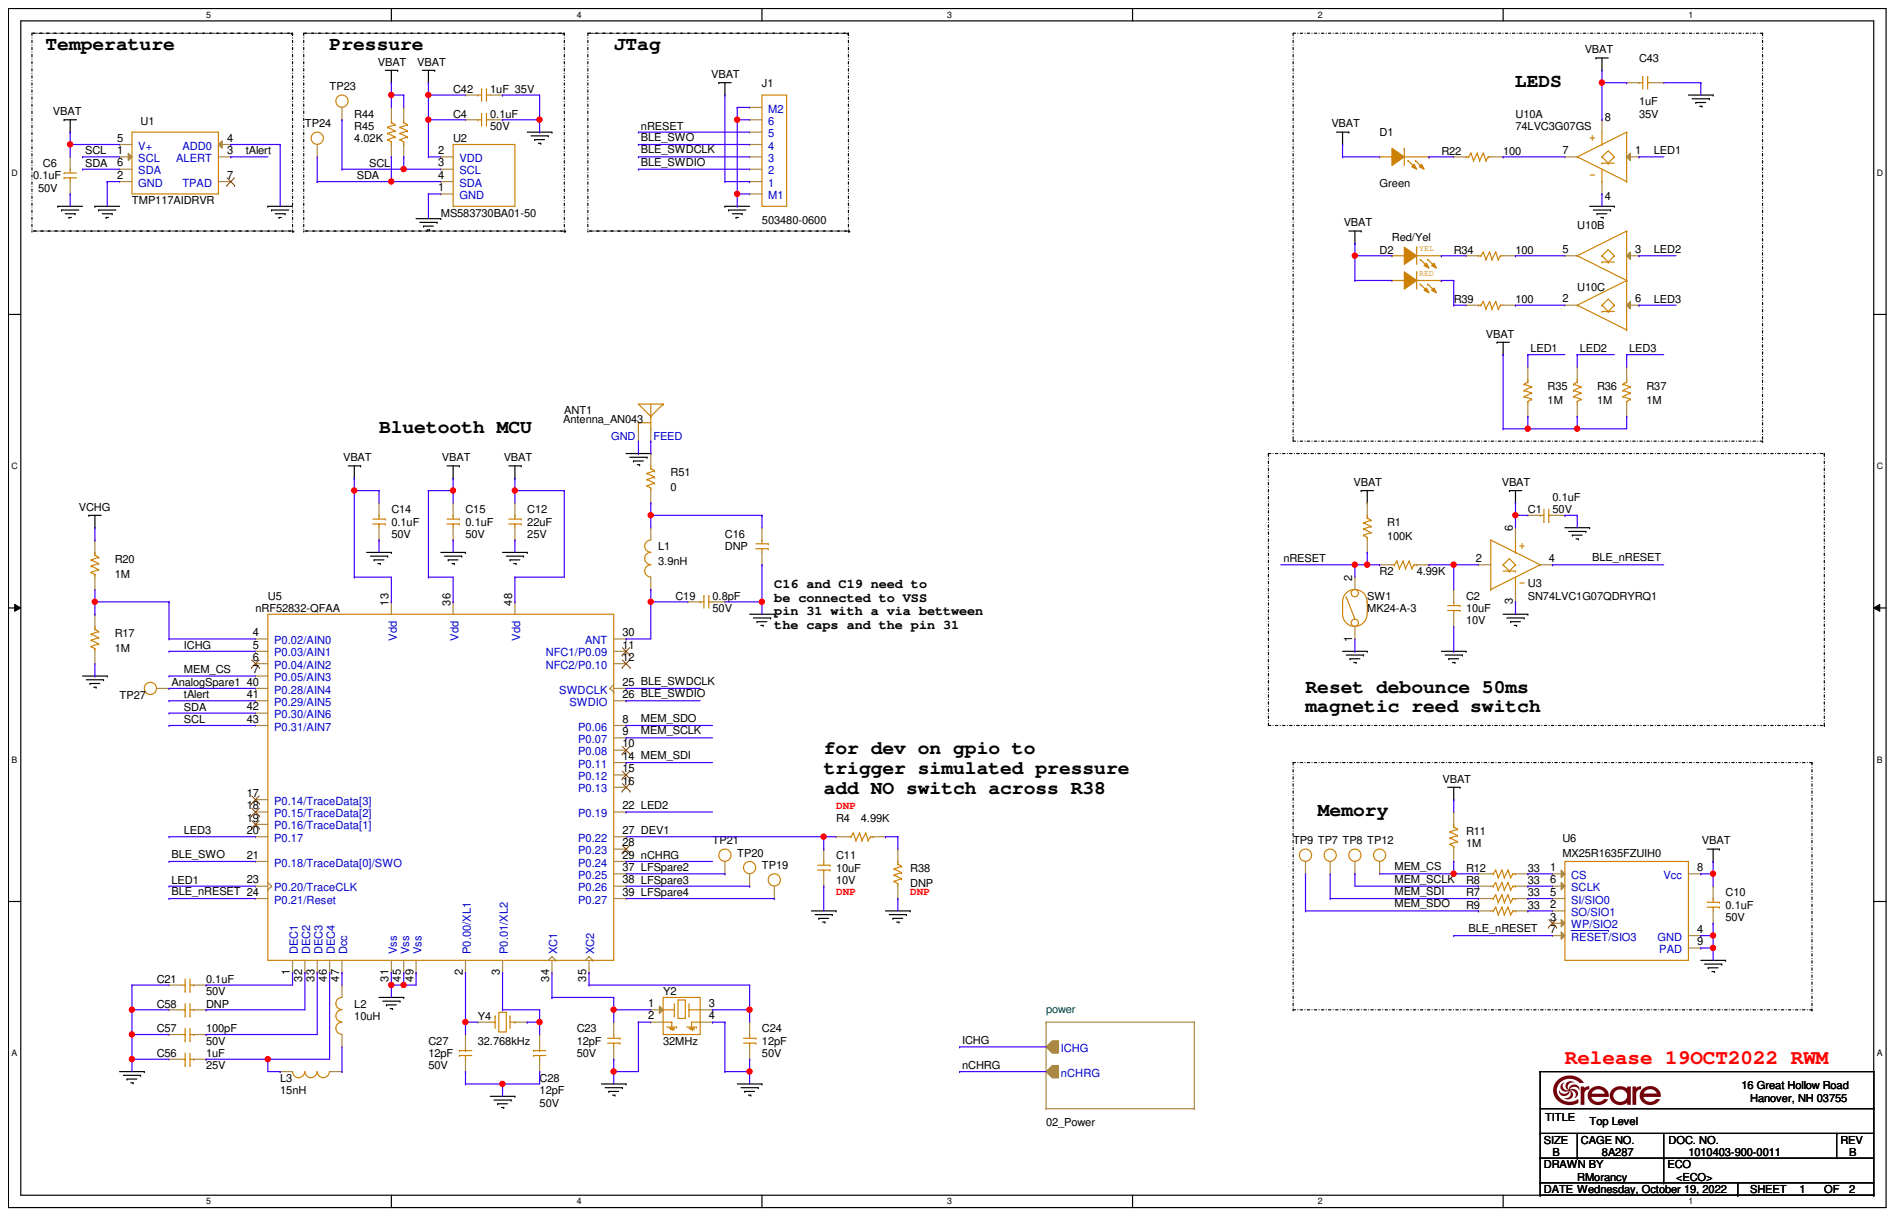
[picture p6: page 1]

C16 and C19 need to
be connected to VSS
pin 31 with a via bettween
the caps and the pin 31

for dev on gpio to
trigger simulated pressure
add NO switch across R38

SIZE SIZE SIZE B B B | CAGE NO. CAGE NO. CAGE NO. 8A287 8A287 8A287 | DOC. NO. DOC. NO. DOC. NO. 1010403-900-0011 1010403-900-0011 1010403-900-0011 | REV REV REV B B B

DRAWN BY DRAWN BY DRAWN BY RMorancy RMorancy RMorancy | | ECO ECO ECO <ECO> <ECO> <ECO>

DATE DATE DATE Wednesday, October 19, 2022 Wednesday, October 19, 2022 Wednesday, October 19, 2022 | SHEET SHEET SHEET 1 1 1 OF OF OF 2 2 2

## Wireless Power

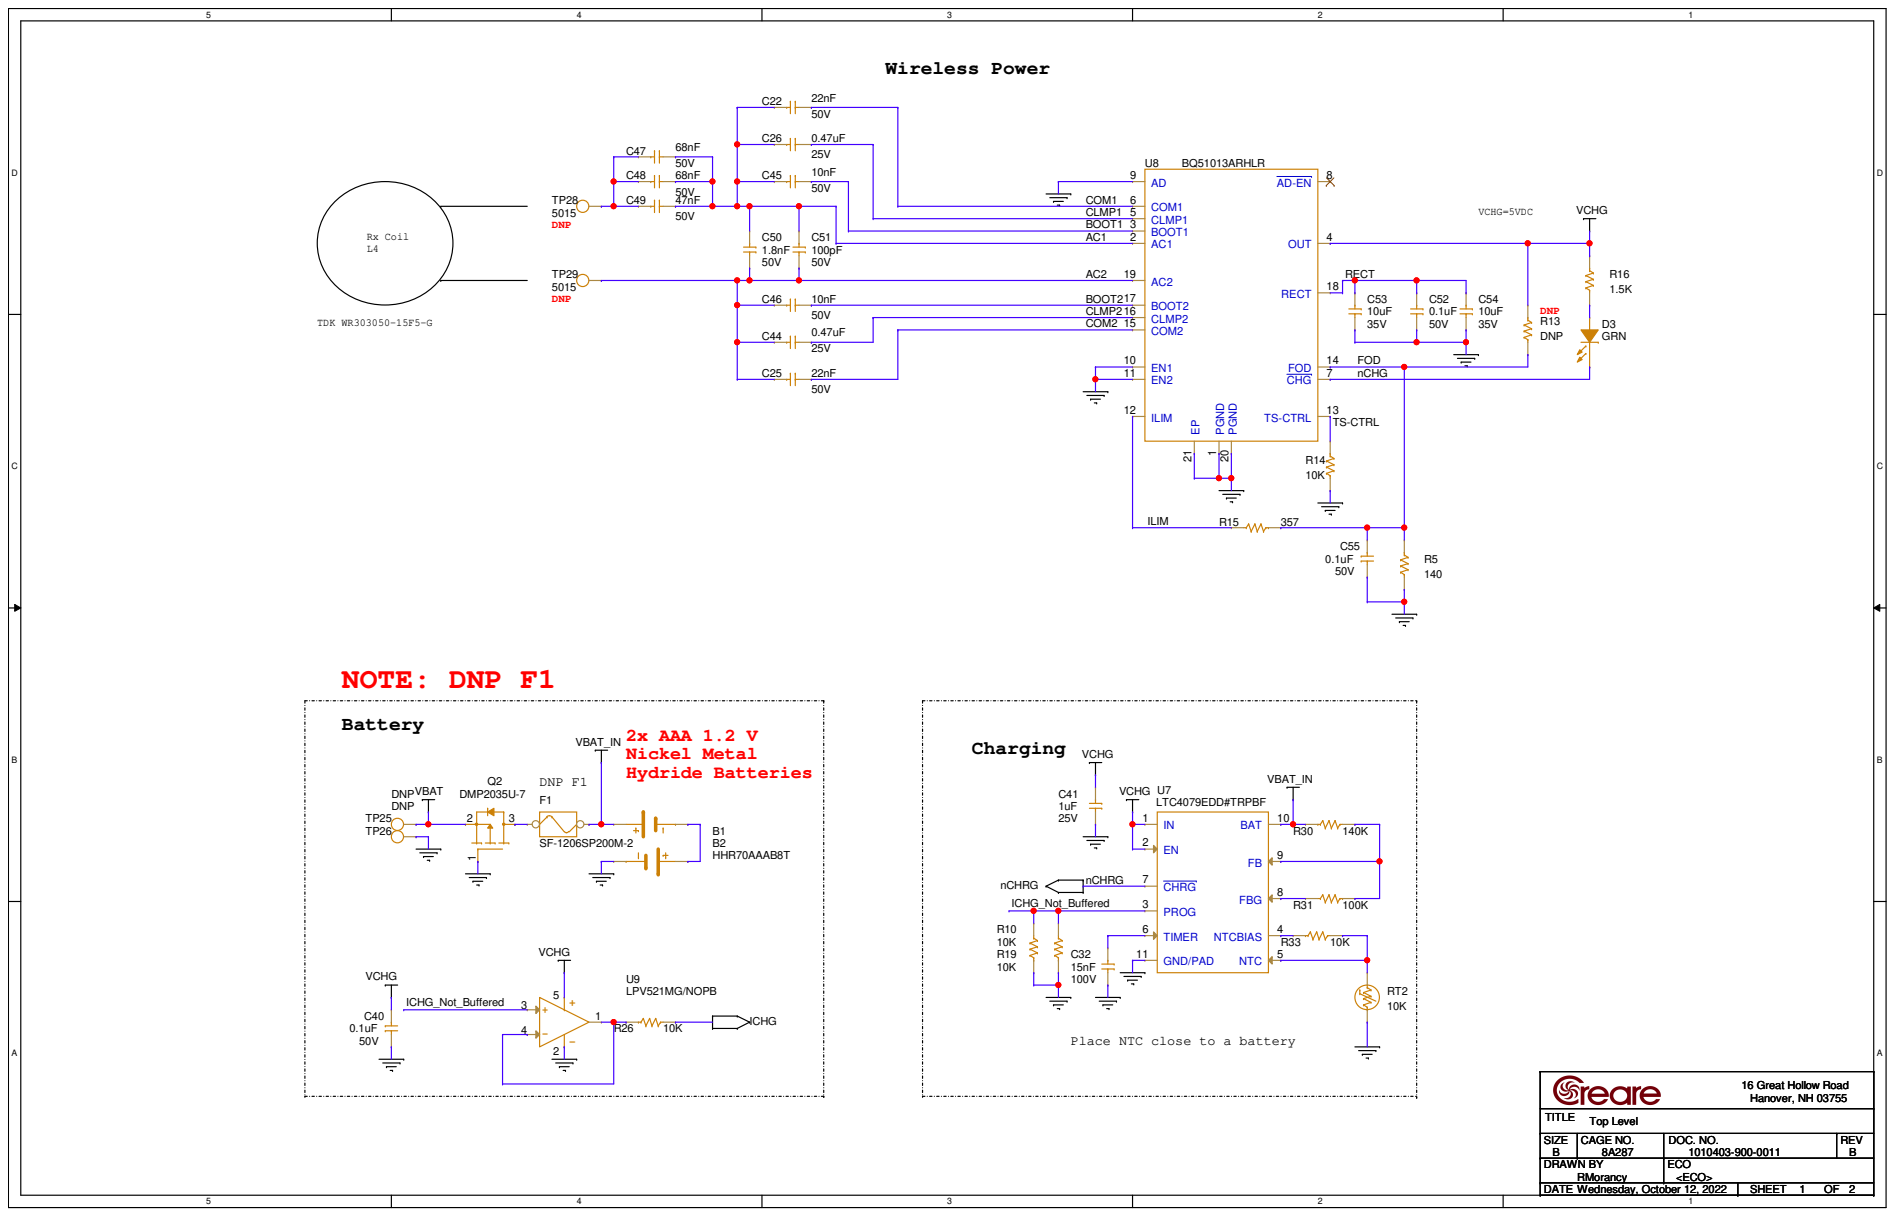
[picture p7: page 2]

Place NTC close to a battery

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

DRAWN BY DRAWN BY DRAWN BY RMorancy RMorancy RMorancy | | ECO ECO ECO <ECO> <ECO> <ECO>

DATE DATE DATE Wednesday, October 12, 2022 Wednesday, October 12, 2022 Wednesday, October 12, 2022 | SHEET SHEET SHEET 1 1 1 OF OF OF 2 2 2

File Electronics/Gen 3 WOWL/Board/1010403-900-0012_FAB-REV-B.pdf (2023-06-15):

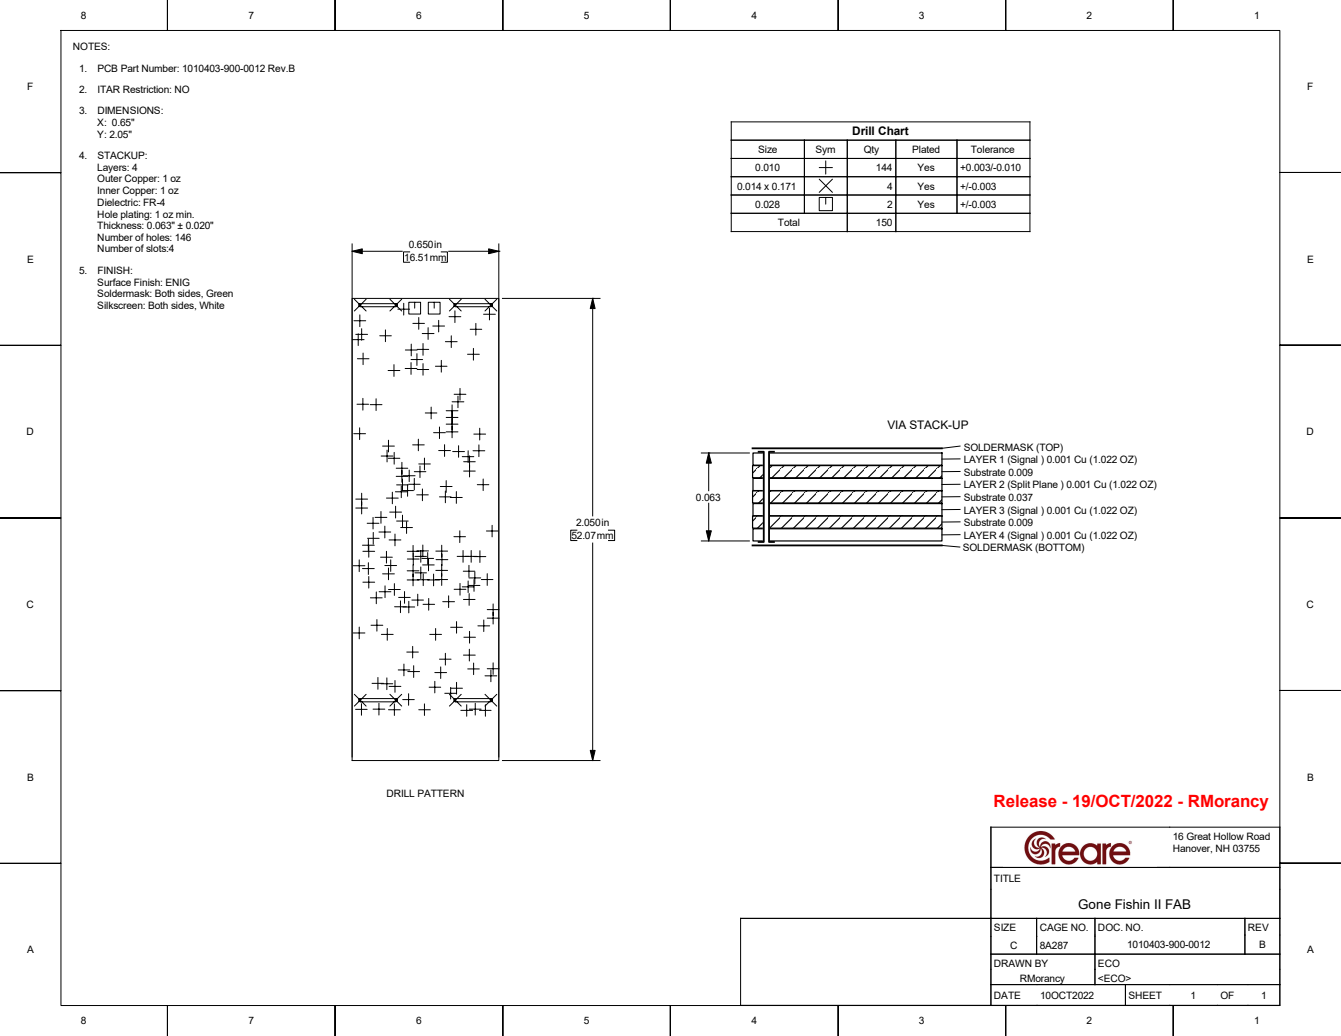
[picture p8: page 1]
NOTES:; 3. DIMENSIONS: X: 0.65" Y: 2.05"; TITLE; DRILL PATTERN; Drill Chart

1. PCB Part Number: 1010403-900-0012 Rev.B

2. ITAR Restriction: NO

4. STACKUP:
Layers: 4
Outer Copper: 1 oz
Inner Copper: 1 oz
Dielectric: FR-4
Hole plating: 1 oz min.
Thickness: 0.063" ± 0.020"
Number of holes: 146
Number of slots:4

Size | Sym | Qty | Plated | Tolerance
0.010 | | | 144 | Yes | +0.003/-0.010
0.014 x 0.171 | | | 4 | Yes | +/-0.003
0.028 | | | | 2 | Yes | +/-0.003
Total | | | | 150

5. FINISH:
Surface Finish: ENIG
Soldermask: Both sides, Green
Silkscreen: Both sides, White

VIA STACK-UP

SOLDERMASK (TOP)
LAYER 1 (Signal ) 0.001 Cu (1.022 OZ)
Substrate 0.009
LAYER 2 (Split Plane ) 0.001 Cu (1.022 OZ)
Substrate 0.037
LAYER 3 (Signal ) 0.001 Cu (1.022 OZ)
LAYER 4 (Signal ) 0.001 Cu (1.022 OZ)
SOLDERMASK (BOTTOM)

Release - 19/OCT/2022 - RMorancy

16 Great Hollow Road
Hanover, NH 03755

Gone Fishin II FAB

SIZE C 8A287 | CAGE NO. | DOC. NO. 1010403-900-0012 | REV B

DRAWN BY RMorancy | | ECO <ECO>

DATE 10OCT2022 | SHEET 1 OF 1

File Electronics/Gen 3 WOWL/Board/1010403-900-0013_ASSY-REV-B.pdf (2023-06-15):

# U5 U⁸ R¹⁶

# D1 Q²

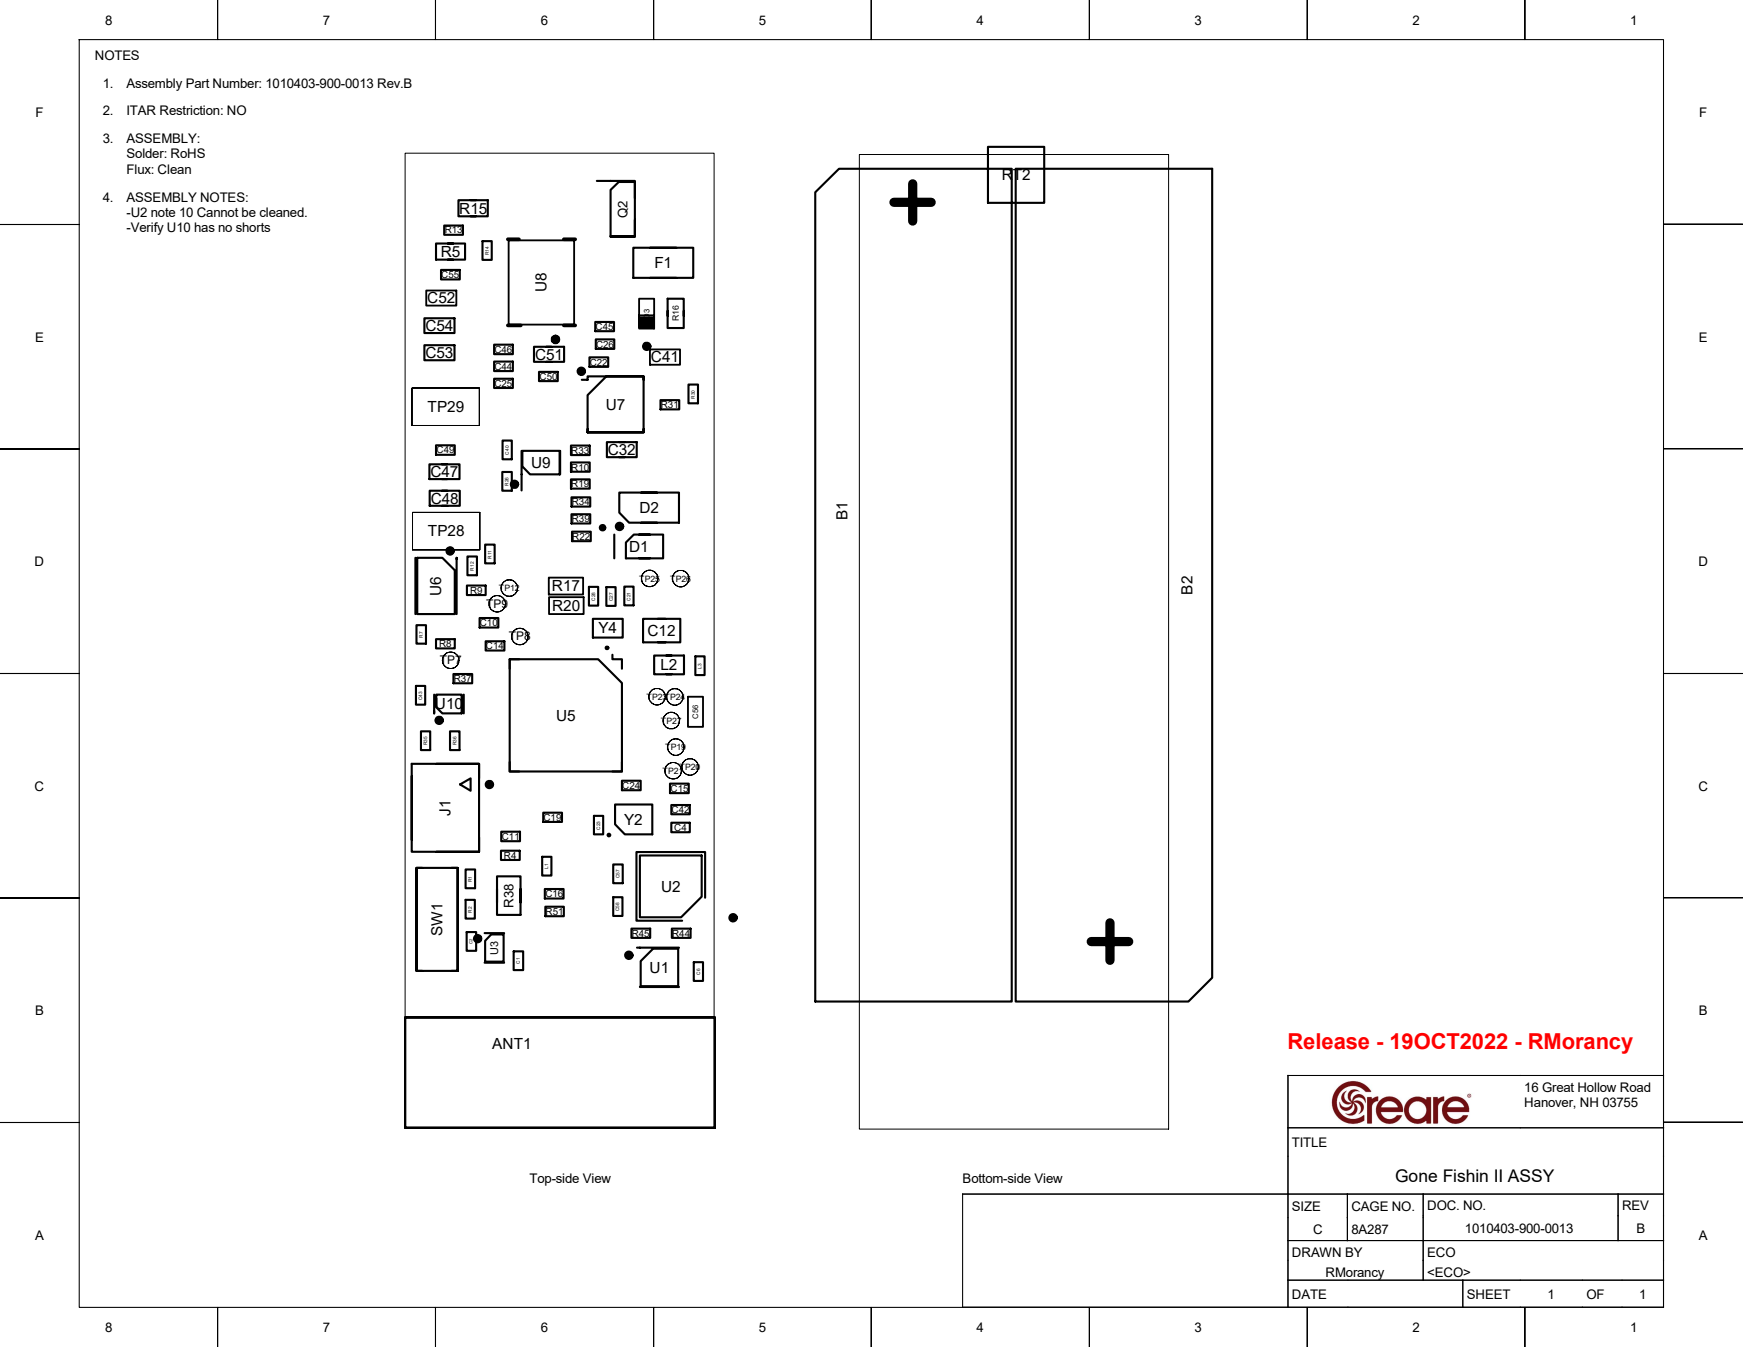
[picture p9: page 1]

1. Assembly Part Number: 1010403-900-0013 Rev.B

4. ASSEMBLY NOTES:
-U2 note 10 Cannot be cleaned.
-Verify U10 has no shorts

Gone Fishin II ASSY

SIZE C 8A287 | CAGE NO. | DOC. NO. 1010403-900-0013 | REV B

DRAWN BY RMorancy | | ECO <ECO>

DATE | SHEET 1 OF 1

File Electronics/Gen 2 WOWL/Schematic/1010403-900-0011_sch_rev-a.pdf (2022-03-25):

Temperature | Pressure
JTag | Testpoints

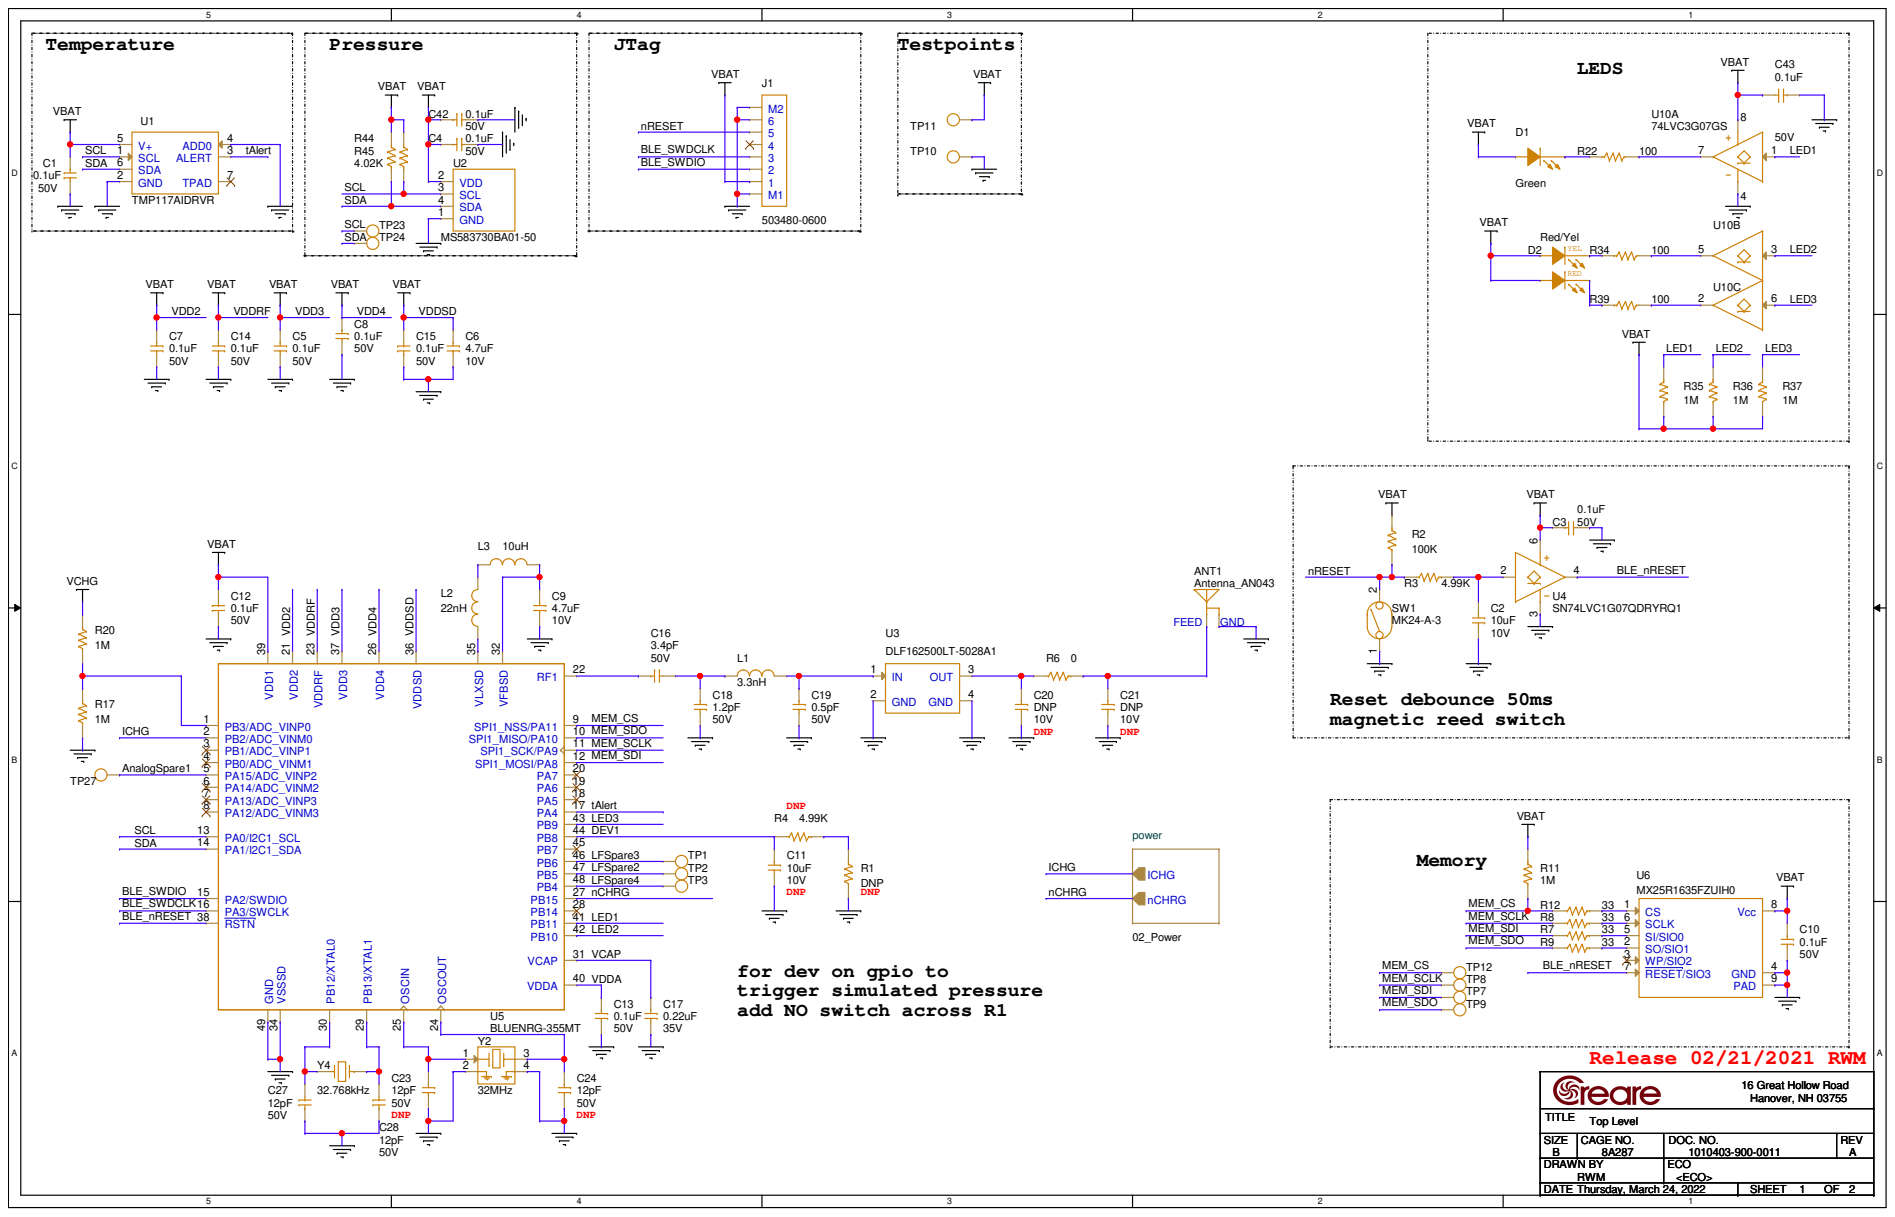
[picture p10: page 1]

for dev on gpio to
trigger simulated pressure
add NO switch across R1

SIZE SIZE SIZE B B B | CAGE NO. CAGE NO. CAGE NO. 8A287 8A287 8A287 | DOC. NO. DOC. NO. DOC. NO. 1010403-900-0011 1010403-900-0011 1010403-900-0011 | REV REV REV A A A

DRAWN BY DRAWN BY DRAWN BY RWM RWM RWM | | ECO ECO ECO <ECO> <ECO> <ECO>

DATE DATE DATE Thursday, March 24, 2022 Thursday, March 24, 2022 Thursday, March 24, 2022 | SHEET SHEET SHEET 1 1 1 OF OF OF 2 2 2

## Wireless Power

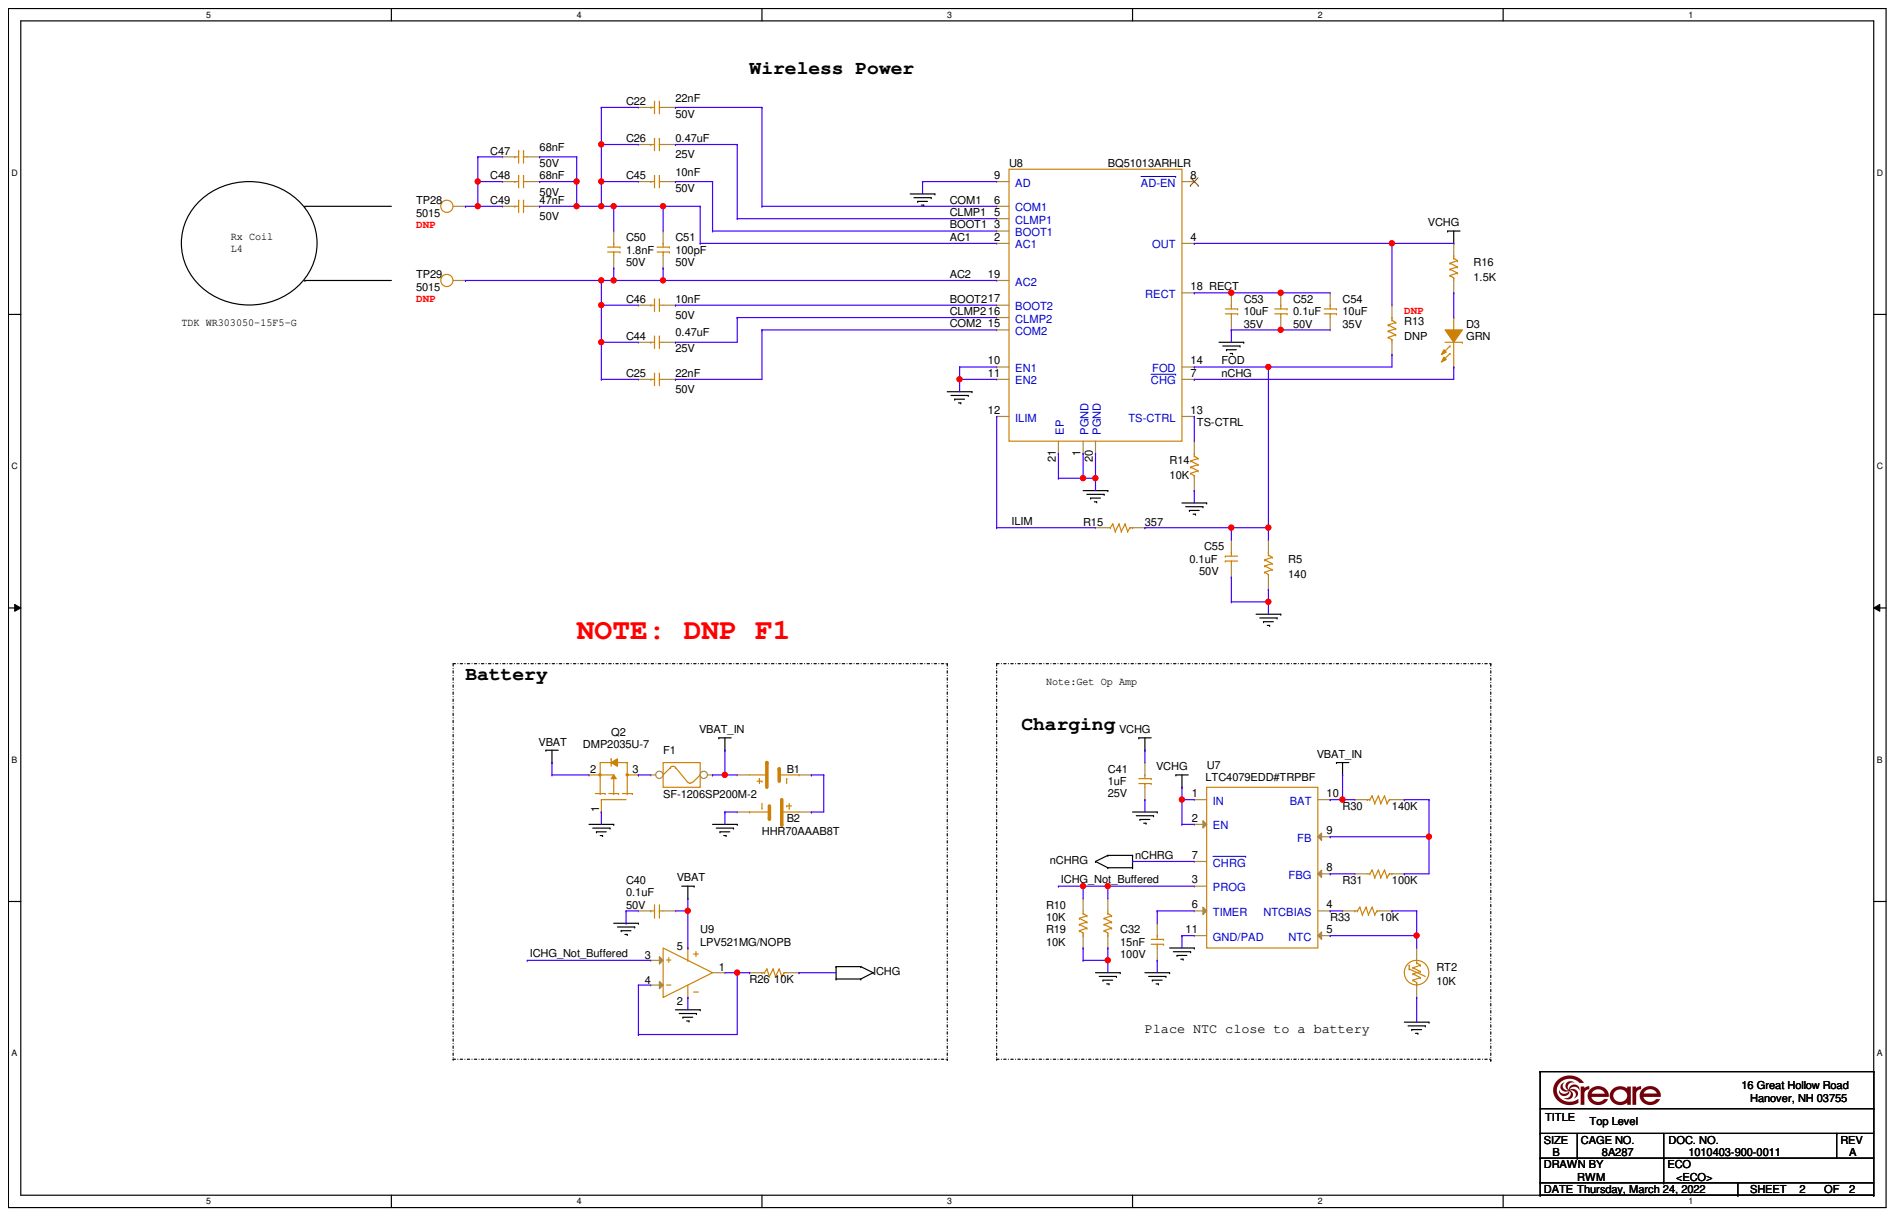
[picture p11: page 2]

Note:Get Op Amp

Place NTC close to a battery

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

DRAWN BY DRAWN BY DRAWN BY RWM RWM RWM | | ECO ECO ECO <ECO> <ECO> <ECO>

DATE DATE DATE Thursday, March 24, 2022 Thursday, March 24, 2022 Thursday, March 24, 2022 | SHEET SHEET SHEET 2 2 2 OF OF OF 2 2 2

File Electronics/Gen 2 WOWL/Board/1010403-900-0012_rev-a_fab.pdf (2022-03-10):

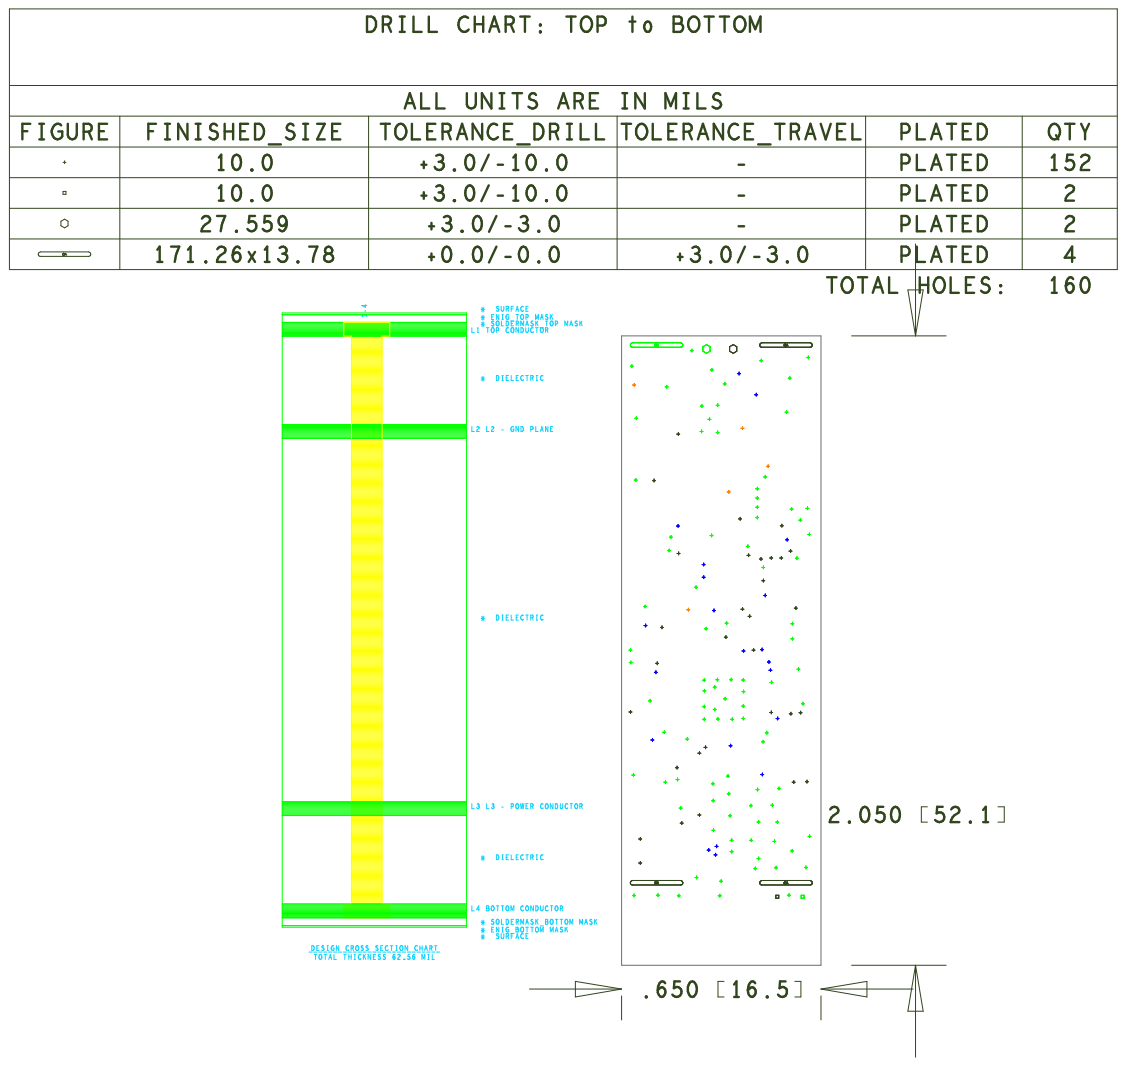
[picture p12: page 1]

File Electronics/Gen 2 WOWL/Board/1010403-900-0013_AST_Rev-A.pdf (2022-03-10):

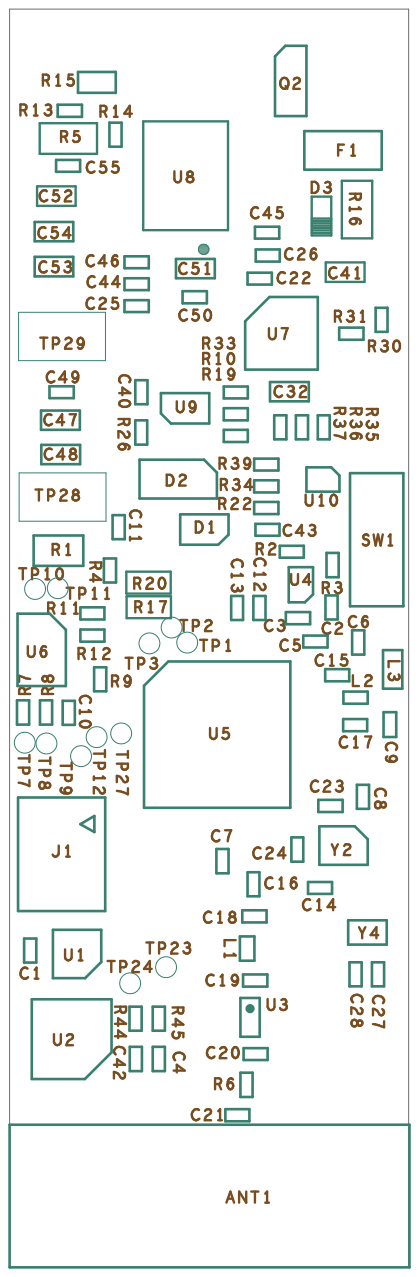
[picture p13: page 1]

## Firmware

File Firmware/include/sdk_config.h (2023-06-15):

/*
	sdk_config.h
	
	Configuration header for the Nordic nRF SDK, for the WOWL sensor.
	
	2020-09-22  WHF  Created.
*/

#ifndef SDK_CONFIG_H
#define SDK_CONFIG_H

#include "wowl.h"

//==========================================================
// <q> BLE_ADVERTISING_ENABLED  - ble_advertising - Advertising module
 

#ifndef BLE_ADVERTISING_ENABLED
#define BLE_ADVERTISING_ENABLED 1
#endif

// <q> BLE_DTM_ENABLED  - ble_dtm - Module for testing RF/PHY using DTM commands
 

#ifndef BLE_DTM_ENABLED
#define BLE_DTM_ENABLED 0
#endif

// <q> BLE_RACP_ENABLED  - ble_racp - Record Access Control Point library
 

#ifndef BLE_RACP_ENABLED
#define BLE_RACP_ENABLED 0
#endif

// <q> NRF_BLE_QWR_ENABLED  - nrf_ble_qwr - Queued writes support module (prepare/execute write)
 

#ifndef NRF_BLE_QWR_ENABLED
#define NRF_BLE_QWR_ENABLED 0
#endif

// <q> PEER_MANAGER_ENABLED  - peer_manager - Peer Manager
 

#ifndef PEER_MANAGER_ENABLED
#define PEER_MANAGER_ENABLED 1
#endif

// </h> 
//==========================================================

// <h> nRF_BLE_Services 

//==========================================================
// <q> BLE_ANCS_C_ENABLED  - ble_ancs_c - Apple Notification Service Client
 

#ifndef BLE_ANCS_C_ENABLED
#define BLE_ANCS_C_ENABLED 0
#endif

// <q> BLE_ANS_C_ENABLED  - ble_ans_c - Alert Notification Service Client
 

#ifndef BLE_ANS_C_ENABLED
#define BLE_ANS_C_ENABLED 0
#endif

// <q> BLE_BAS_C_ENABLED  - ble_bas_c - Battery Service Client
 

#ifndef BLE_BAS_C_ENABLED
#define BLE_BAS_C_ENABLED 0
#endif

// <q> BLE_BAS_ENABLED  - ble_bas - Battery Service
 

#ifndef BLE_BAS_ENABLED
#define BLE_BAS_ENABLED 0
#endif

// <q> BLE_CSCS_ENABLED  - ble_cscs - Cycling Speed and Cadence Service
 

#ifndef BLE_CSCS_ENABLED
#define BLE_CSCS_ENABLED 0
#endif

// <q> BLE_CTS_C_ENABLED  - ble_cts_c - Current Time Service Client
 

#ifndef BLE_CTS_C_ENABLED
#define BLE_CTS_C_ENABLED 0
#endif

// <q> BLE_DIS_ENABLED  - ble_dis - Device Information Service
 

#ifndef BLE_DIS_ENABLED
#define BLE_DIS_ENABLED 1
#endif

// <q> BLE_GLS_ENABLED  - ble_gls - Glucose Service
 

#ifndef BLE_GLS_ENABLED
#define BLE_GLS_ENABLED 0
#endif

// <q> BLE_HIDS_ENABLED  - ble_hids - Human Interface Device Service
 

#ifndef BLE_HIDS_ENABLED
#define BLE_HIDS_ENABLED 0
#endif

// <q> BLE_HRS_C_ENABLED  - ble_hrs_c - Heart Rate Service Client
 

#ifndef BLE_HRS_C_ENABLED
#define BLE_HRS_C_ENABLED 0
#endif

// <q> BLE_HRS_ENABLED  - ble_hrs - Heart Rate Service
 

#ifndef BLE_HRS_ENABLED
#define BLE_HRS_ENABLED 0
#endif

// <q> BLE_HTS_ENABLED  - ble_hts - Health Thermometer Service
 

#ifndef BLE_HTS_ENABLED
#define BLE_HTS_ENABLED 0
#endif

// <q> BLE_IAS_C_ENABLED  - ble_ias_c - Immediate Alert Service Client
 

#ifndef BLE_IAS_C_ENABLED
#define BLE_IAS_C_ENABLED 0
#endif

// <q> BLE_IAS_ENABLED  - ble_ias - Immediate Alert Service
 

#ifndef BLE_IAS_ENABLED
#define BLE_IAS_ENABLED 0
#endif

// <q> BLE_LBS_C_ENABLED  - ble_lbs_c - Nordic LED Button Service Client
 

#ifndef BLE_LBS_C_ENABLED
#define BLE_LBS_C_ENABLED 0
#endif

// <q> BLE_LBS_ENABLED  - ble_lbs - LED Button Service
 

#ifndef BLE_LBS_ENABLED
#define BLE_LBS_ENABLED 0
#endif

// <q> BLE_LLS_ENABLED  - ble_lls - Link Loss Service
 

#ifndef BLE_LLS_ENABLED
#define BLE_LLS_ENABLED 0
#endif

// <q> BLE_NUS_C_ENABLED  - ble_nus_c - Nordic UART Central Service
 

#ifndef BLE_NUS_C_ENABLED
#define BLE_NUS_C_ENABLED 0
#endif

// <q> BLE_NUS_ENABLED  - ble_nus - Nordic UART Service
 

#ifndef BLE_NUS_ENABLED
#define BLE_NUS_ENABLED 0
#endif

// <q> BLE_RSCS_C_ENABLED  - ble_rscs_c - Running Speed and Cadence Client
 

#ifndef BLE_RSCS_C_ENABLED
#define BLE_RSCS_C_ENABLED 0
#endif

// <q> BLE_RSCS_ENABLED  - ble_rscs - Running Speed and Cadence Service
 

#ifndef BLE_RSCS_ENABLED
#define BLE_RSCS_ENABLED 0
#endif

// <q> BLE_TPS_ENABLED  - ble_tps - TX Power Service
 

#ifndef BLE_TPS_ENABLED
#define BLE_TPS_ENABLED 0
#endif

// </h> 
//==========================================================

// <h> nRF_Drivers 

//==========================================================
// <e> ADC_ENABLED - nrf_drv_adc - Driver for ADC peripheral (nRF51)
//==========================================================
#ifndef ADC_ENABLED
#define ADC_ENABLED 0
#endif
#if  ADC_ENABLED
// <o> ADC_CONFIG_IRQ_PRIORITY  - Interrupt priority
 

// <i> Priorities 0,2 (nRF51) and 0,1,4,5 (nRF52) are reserved for SoftDevice
// <0=> 0 (highest) 
// <1=> 1 
// <2=> 2 
// <3=> 3 
// <4=> 4 
// <5=> 5 
// <6=> 6 
// <7=> 7 

#ifndef ADC_CONFIG_IRQ_PRIORITY
#define ADC_CONFIG_IRQ_PRIORITY 6
#endif

#endif //ADC_ENABLED
// </e>

// <e> CLOCK_ENABLED - nrf_drv_clock - CLOCK peripheral driver
//==========================================================
#ifndef CLOCK_ENABLED
#define CLOCK_ENABLED 1
#endif
#if  CLOCK_ENABLED
// <o> CLOCK_CONFIG_XTAL_FREQ  - HF XTAL Frequency
 
// <0=> Default (64 MHz) 

#ifndef CLOCK_CONFIG_XTAL_FREQ
#define CLOCK_CONFIG_XTAL_FREQ 0
#endif

// <o> CLOCK_CONFIG_LF_SRC  - LF Clock Source
 
// <0=> RC 
// <1=> XTAL 
// <2=> Synth 

#ifndef CLOCK_CONFIG_LF_SRC
#define CLOCK_CONFIG_LF_SRC 1
#endif

// <o> CLOCK_CONFIG_IRQ_PRIORITY  - Interrupt priority
 

// <i> Priorities 0,2 (nRF51) and 0,1,4,5 (nRF52) are reserved for SoftDevice
// <0=> 0 (highest) 
// <1=> 1 
// <2=> 2 
// <3=> 3 
// <4=> 4 
// <5=> 5 
// <6=> 6 
// <7=> 7 

#ifndef CLOCK_CONFIG_IRQ_PRIORITY
#define CLOCK_CONFIG_IRQ_PRIORITY 6
#endif

#endif //CLOCK_ENABLED
// </e>

// <e> COMP_ENABLED - nrf_drv_comp - COMP peripheral driver
//==========================================================
#ifndef COMP_ENABLED
#define COMP_ENABLED 0
#endif
#if  COMP_ENABLED
// <o> COMP_CONFIG_REF  - Reference voltage
 
// <0=> Internal 1.2V 
// <1=> Internal 1.8V 
// <2=> Internal 2.4V 
// <4=> VDD 
// <7=> ARef 

#ifndef COMP_CONFIG_REF
#define COMP_CONFIG_REF 1
#endif

// <o> COMP_CONFIG_MAIN_MODE  - Main mode
 
// <0=> Single ended 
// <1=> Differential 

#ifndef COMP_CONFIG_MAIN_MODE
#define COMP_CONFIG_MAIN_MODE 0
#endif

// <o> COMP_CONFIG_SPEED_MODE  - Speed mode
 
// <0=> Low power 
// <1=> Normal 
// <2=> High speed 

#ifndef COMP_CONFIG_SPEED_MODE
#define COMP_CONFIG_SPEED_MODE 2
#endif

// <o> COMP_CONFIG_HYST  - Hystheresis
 
// <0=> No 
// <1=> 50mV 

#ifndef COMP_CONFIG_HYST
#define COMP_CONFIG_HYST 0
#endif

// <o> COMP_CONFIG_ISOURCE  - Current Source
 
// <0=> Off 
// <1=> 2.5 uA 
// <2=> 5 uA 
// <3=> 10 uA 

#ifndef COMP_CONFIG_ISOURCE
#define COMP_CONFIG_ISOURCE 0
#endif

// <o> COMP_CONFIG_INPUT  - Analog input
 
// <0=> 0 
// <1=> 1 
// <2=> 2 
// <3=> 3 
// <4=> 4 
// <5=> 5 
// <6=> 6 
// <7=> 7 

#ifndef COMP_CONFIG_INPUT
#define COMP_CONFIG_INPUT 0
#endif

// <o> COMP_CONFIG_IRQ_PRIORITY  - Interrupt priority
 

// <i> Priorities 0,2 (nRF51) and 0,1,4,5 (nRF52) are reserved for SoftDevice
// <0=> 0 (highest) 
// <1=> 1 
// <2=> 2 
// <3=> 3 
// <4=> 4 
// <5=> 5 
// <6=> 6 
// <7=> 7 

#ifndef COMP_CONFIG_IRQ_PRIORITY
#define COMP_CONFIG_IRQ_PRIORITY 6
#endif

#endif //COMP_ENABLED
// </e>

// <q> EGU_ENABLED  - nrf_drv_swi - SWI(EGU) peripheral driver
 

#ifndef EGU_ENABLED
#define EGU_ENABLED 0
#endif

// <e> GPIOTE_ENABLED - nrf_drv_gpiote - GPIOTE peripheral driver
//==========================================================
#ifndef GPIOTE_ENABLED
#define GPIOTE_ENABLED 1
#endif
#if  GPIOTE_ENABLED
// <o> GPIOTE_CONFIG_NUM_OF_LOW_POWER_EVENTS - Number of lower power input pins 
#ifndef GPIOTE_CONFIG_NUM_OF_LOW_POWER_EVENTS
#define GPIOTE_CONFIG_NUM_OF_LOW_POWER_EVENTS 4
#endif

// <o> GPIOTE_CONFIG_IRQ_PRIORITY  - Interrupt priority
 

// <i> Priorities 0,2 (nRF51) and 0,1,4,5 (nRF52) are reserved for SoftDevice
// <0=> 0 (highest) 
// <1=> 1 
// <2=> 2 
// <3=> 3 
// <4=> 4 
// <5=> 5 
// <6=> 6 
// <7=> 7 

#ifndef GPIOTE_CONFIG_IRQ_PRIORITY
#define GPIOTE_CONFIG_IRQ_PRIORITY 2
#endif

#endif //GPIOTE_ENABLED
// </e>

// <e> I2S_ENABLED - nrf_drv_i2s - I2S peripheral driver
//==========================================================
#ifndef I2S_ENABLED
#define I2S_ENABLED                                                       0
#endif


// <e> LPCOMP_ENABLED - nrf_drv_lpcomp - LPCOMP peripheral driver
//==========================================================
#ifndef LPCOMP_ENABLED
#define LPCOMP_ENABLED 0
#endif
#if  LPCOMP_ENABLED
// <o> LPCOMP_CONFIG_REFERENCE  - Reference voltage
 
// <0=> Supply 1/8 
// <1=> Supply 2/8 
// <2=> Supply 3/8 
// <3=> Supply 4/8 
// <4=> Supply 5/8 
// <5=> Supply 6/8 
// <6=> Supply 7/8 
// <8=> Supply 1/16 (nRF52) 
// <9=> Supply 3/16 (nRF52) 
// <10=> Supply 5/16 (nRF52) 
// <11=> Supply 7/16 (nRF52) 
// <12=> Supply 9/16 (nRF52) 
// <13=> Supply 11/16 (nRF52) 
// <14=> Supply 13/16 (nRF52) 
// <15=> Supply 15/16 (nRF52) 
// <7=> External Ref 0 
// <65543=> External Ref 1 

#ifndef LPCOMP_CONFIG_REFERENCE
#define LPCOMP_CONFIG_REFERENCE 3
#endif

// <o> LPCOMP_CONFIG_DETECTION  - Detection
 
// <0=> Crossing 
// <1=> Up 
// <2=> Down 

#ifndef LPCOMP_CONFIG_DETECTION
#define LPCOMP_CONFIG_DETECTION 2
#endif

// <o> LPCOMP_CONFIG_INPUT  - Analog input
 
// <0=> 0 
// <1=> 1 
// <2=> 2 
// <3=> 3 
// <4=> 4 
// <5=> 5 
// <6=> 6 
// <7=> 7 

#ifndef LPCOMP_CONFIG_INPUT
#define LPCOMP_CONFIG_INPUT 0
#endif

// <o> LPCOMP_CONFIG_IRQ_PRIORITY  - Interrupt priority
 

// <i> Priorities 0,2 (nRF51) and 0,1,4,5 (nRF52) are reserved for SoftDevice
// <0=> 0 (highest) 
// <1=> 1 
// <2=> 2 
// <3=> 3 
// <4=> 4 
// <5=> 5 
// <6=> 6 
// <7=> 7 

#ifndef LPCOMP_CONFIG_IRQ_PRIORITY
#define LPCOMP_CONFIG_IRQ_PRIORITY 6
#endif

#endif //LPCOMP_ENABLED
// </e>

// <e> PDM_ENABLED - nrf_drv_pdm - PDM peripheral driver
//==========================================================
#ifndef PDM_ENABLED
#define PDM_ENABLED 0
#endif
#if  PDM_ENABLED
// <o> PDM_CONFIG_MODE  - Mode
 
// <0=> Stereo 
// <1=> Mono 

#ifndef PDM_CONFIG_MODE
#define PDM_CONFIG_MODE 1
#endif

// <o> PDM_CONFIG_EDGE  - Edge
 
// <0=> Left falling 
// <1=> Left rising 

#ifndef PDM_CONFIG_EDGE
#define PDM_CONFIG_EDGE 0
#endif

// <o> PDM_CONFIG_CLOCK_FREQ  - Clock frequency
 
// <134217728=> 1000k 
// <138412032=> 1032k (default) 
// <142606336=> 1067k 

#ifndef PDM_CONFIG_CLOCK_FREQ
#define PDM_CONFIG_CLOCK_FREQ 138412032
#endif

// <o> PDM_CONFIG_IRQ_PRIORITY  - Interrupt priority
 

// <i> Priorities 0,2 (nRF51) and 0,1,4,5 (nRF52) are reserved for SoftDevice
// <0=> 0 (highest) 
// <1=> 1 
// <2=> 2 
// <3=> 3 
// <4=> 4 
// <5=> 5 
// <6=> 6 
// <7=> 7 

#ifndef PDM_CONFIG_IRQ_PRIORITY
#define PDM_CONFIG_IRQ_PRIORITY 6
#endif

#endif //PDM_ENABLED
// </e>

// <q> PERIPHERAL_RESOURCE_SHARING_ENABLED  - nrf_drv_common - Peripheral drivers common module
 

#ifndef PERIPHERAL_RESOURCE_SHARING_ENABLED
#define PERIPHERAL_RESOURCE_SHARING_ENABLED 0
#endif

// <q> PPI_ENABLED  - nrf_drv_ppi - PPI peripheral driver
 

#ifndef PPI_ENABLED
#define PPI_ENABLED 0
#endif

// <e> PWM_ENABLED - nrf_drv_pwm - PWM peripheral driver
//==========================================================
#ifndef PWM_ENABLED
#define PWM_ENABLED 0
#endif
#if  PWM_ENABLED
// <o> PWM_DEFAULT_CONFIG_OUT0_PIN - Out0 pin  <0-31> 


#ifndef PWM_DEFAULT_CONFIG_OUT0_PIN
#define PWM_DEFAULT_CONFIG_OUT0_PIN 31
#endif

// <o> PWM_DEFAULT_CONFIG_OUT1_PIN - Out1 pin  <0-31> 


#ifndef PWM_DEFAULT_CONFIG_OUT1_PIN
#define PWM_DEFAULT_CONFIG_OUT1_PIN 31
#endif

// <o> PWM_DEFAULT_CONFIG_OUT2_PIN - Out2 pin  <0-31> 


#ifndef PWM_DEFAULT_CONFIG_OUT2_PIN
#define PWM_DEFAULT_CONFIG_OUT2_PIN 31
#endif

// <o> PWM_DEFAULT_CONFIG_OUT3_PIN - Out3 pin  <0-31> 


#ifndef PWM_DEFAULT_CONFIG_OUT3_PIN
#define PWM_DEFAULT_CONFIG_OUT3_PIN 31
#endif

// <o> PWM_DEFAULT_CONFIG_BASE_CLOCK  - Base clock
 
// <0=> 16 MHz 
// <1=> 8 MHz 
// <2=> 4 MHz 
// <3=> 2 MHz 
// <4=> 1 MHz 
// <5=> 500 kHz 
// <6=> 250 kHz 
// <7=> 125 MHz 

#ifndef PWM_DEFAULT_CONFIG_BASE_CLOCK
#define PWM_DEFAULT_CONFIG_BASE_CLOCK 4
#endif

// <o> PWM_DEFAULT_CONFIG_COUNT_MODE  - Count mode
 
// <0=> Up 
// <1=> Up and Down
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

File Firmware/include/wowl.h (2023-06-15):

/*
	wowl.h
	
	Declarations for the WOWL sensor.
	
	2020-09-22  WHF  Created.
*/

#ifndef __WOWL_H__
#define __WOWL_H__

#include "wowlCodes.h"

#include <assert.h>
#include <stdbool.h>
#include <stdint.h>
#include <string.h>

#include <cmsis_compiler.h>

#include <nordic_common.h>
#include <nrf_gpiote.h>

//********************************  Constants  *******************************//

// Set to 1 to enable unit tests.
#define DO_TESTS                                                          0


// Number of milliseconds in a second.
#define MSEC_PER_SEC                                                  1000u


/////  Pin Allocations  /////
// Pin numbers for functions.  Pins on the NRF52 are numbered 0 through 31.
//  NOTE: these are the GPIO pin IDs, not the package pin numbers.
//  See the schematic 1010403-900-0011 Rev B for the net names.

// TODO: verify after Released schematic available!

#define PIN_AN_VCHG                                                       2
#define PIN_AN_ICHG                                                       3
#define PIN_reserved_4                                                    4
#define PIN_MEM_nCS                                                       5
#define PIN_MEM_SDO                                                       6
#define PIN_MEM_SCLK                                                      7
#define PIN_reserved_8                                                    8
#define PIN_reserved_9                                                    9
#define PIN_reserved_10                                                  10
#define PIN_MEM_SDI                                                      11
#define PIN_reserved_12                                                  12
#define PIN_reserved_13                                                  13
#define PIN_reserved_14                                                  14
#define PIN_reserved_15                                                  15
#define PIN_reserved_16                                                  16
#define PIN_LED_RED                                                      17
#define PIN_reserved_swo                                                 18
#define PIN_LED_YEL                                                      19
#define PIN_LED_GRN                                                      20
#define PIN_BLE_nRESET                                                   21
#define PIN_SUBMERGE_TEST                                                22
#define PIN_reserved_23                                                  23
#define PIN_nCHRG                                                        24
#define PIN_TP21                                                         25
#define PIN_TP20                                                         26
#define PIN_TP19                                                         27
#define PIN_TP27                                                         28
#define PIN_T_ALERT                                                      29
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

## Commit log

2020-12-29 add hardware and software files
    [1010309-900-0010_Rev-A.xlsx, 1010309-900-0011_Rev-A.DSN, 1010309-900-0012_Rev-A-1-4.drl, 1010309-900-0012_Rev-A.brd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]
2022-03-10 Adding python code that connects to WOWLs and downloads data. Currently there is a bug with windows and it does not run. Fixes will be coming soon.
2022-03-10 rearrange electronics folder
    [1010309-900-0010_Rev-A.xlsx, 1010309-900-0011_Rev-A.DSN, 1010309-900-0012_Rev-A-1-4.drl, 1010309-900-0012_Rev-A.brd]
2022-03-10 BOM, schematic, layout for Gen 2 board
    [1010403-900-0010_Rev-A.xlsx, 1010403-900-0011_Sch_Rev-A.DSN, 1010403-900-0012_rev-a.brd]
2023-05-03 add ICD and clean up
    [Vacuum_Mold_Positive.STEP, WOWL Mold KO.STEP, WOWL Mold Outer.STEP, WOWL Mold.STEP]
2023-06-15 Adding Gen 3 resources
    [1010403-900-0010_REV_B.xlsx]
